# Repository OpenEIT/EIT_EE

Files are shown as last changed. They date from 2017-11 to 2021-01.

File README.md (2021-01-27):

# Spectra PDF

The schematic for the 32 electrode EIT system is called Spectra.pdf and is contained in the top level directory. Please let me know if you think it should have any modifications. 

# Eagle_EIT

Note: the following design is an older design for an 8 electrode system. I have a newer better system which was designed in Altium which I'll put up here as soon as crowd supply campaign finalized. In the meantime I'd love it if you wanted to join the mailing list! 

https://www.crowdsupply.com/mindseye-biomedical/spectra

## EIT PCB design in Eagle CAD

Electrical Impedance Tomography is a new way to image conductivity changes inside any mostly liquid medium - such as the human body. It's attractive as it doesn't use ionizing radiation like the X-rays used in a CATSCAN, and could be relatively cheap to mass produce. 

This project is an example of a working system from PCB to firmware to reconstruction algorithm. Further work could certainly improve the resolution, but for now we have functionality in all sub sections. 

This is everything required for the basic 8 electrode design to work. Photo of the assembled PCB included. 

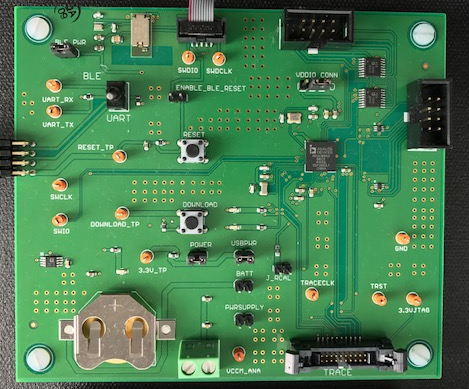
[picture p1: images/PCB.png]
EIT PCB


The design is based on the ADuCM350 which has a dedicated high precision front end with 16 bit resolution 160 kSPS data speed.The front end also performs a DFT at the rate of 13.8ms per calculation. This leads to a high performance minimal noise set up, excellent for both R&D or educational purposes. 

In the not too distant future kits may be available with a smaller version of the PCB mounted in a box, an electrode harness for mounting to the body, and all cables required to run. 

This combination would be an excellent educational tool for those researching this area, as it allows you to try most of the reconstruction algorithms or come up with your own and quantify any improvements in results. 

It's the same technique as is used in CATSCAN's, except the current running through the body instead of dangerous ionizing radiation of X-Rays. 

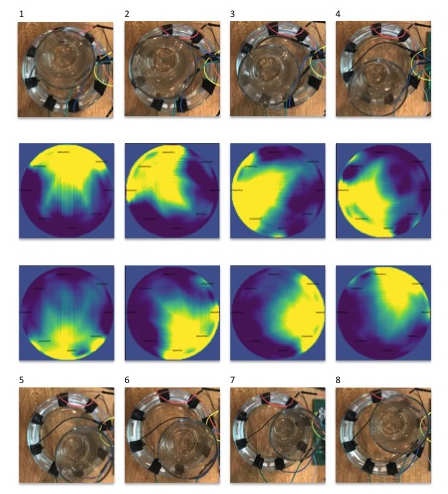
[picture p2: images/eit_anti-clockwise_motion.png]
EIT example


Improvements are welcome to this design. To increase resolution you could make a rotational version which is time resolution limited, or simply add more electrodes and re-compute the reconstruction that way. Another intended improvement is to move to tetrapolar differential electrodes set up. If you'd like to collaborate just pull the repository or email contact@mindseyebiomedical.com

We'd love to hear how you are using this! 

## New Board Design 

We have a newer better board design which is uploaded and called Spectra.pdf. Check it out. 

## Future Plans 

Are hatching! Join the technical discussion list to discuss further at openeit.github.io 

## License 

The Creative Commons Attribution-NonCommercial-ShareAlike 4.0 International License seems to fit best with this project. Check out the human readable summary here: 

<br />This work is licensed under a <a rel="license" href="http://creativecommons.org/licenses/by-nc-sa/4.0/">Creative Commons Attribution-NonCommercial-ShareAlike 4.0 International License</a>.

If you'd like to make a derivative of this project in a commercial setting, we'd love a payment so that we can afford to spend time both maintaining this project and making more projects like this one. If this hybrid open source model works, it would enable open source projects to receive some funding, making the global commons stronger to benefit everyone.

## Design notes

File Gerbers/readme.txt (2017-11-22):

board stackup

1. top layer
2. inner layer pwr
3. inner layer gnd
16. bottom layer

TOP SIDE  *.GTL
inner layer 2  *.G2L
inner layer 3  *.G3L
BOTTOM SIDE  *.GBL
silkscreen top side  *.GTO
solder stop mask top *.GTS
solder stop mask bottom *.GBS
cream frame top  *.GTC
board outline *.GKO
excellent drill file *.drd
component placement list top	  *.mnt
component placement list bottom *.mnb

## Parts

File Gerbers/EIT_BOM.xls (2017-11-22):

Qty-1 | Part References | Value | Package | Mfg Part Num | Mfg Name | VID | Vendor Part Num | Description | Pkg Code
1 | CR2032 |  | CR2032-SMD | 3002TR | Keystone Electronics | DK | 36-3002CT-ND | HOLDER BATTERY COIN 20MM DIA SMD | Surface Mount Coincell Holder
2 | AFE, M1 |  | 2X04SHROUDED | 61200821621 | Wurth Electronics | DK | 732-5395-ND | 8 Positions Header Shrouded Connector 0.100 2.54mm Through Hole | Through Hole
1 | PWRLED |  | 0603_LED | 150060BS75000 | Wurth Electronics | DK | 732-4966-1-ND | LED BLUE CLEAR 0603 SMD | 0603 1608 Metric
1 | LED2 |  | 0603_LED | 150060GS75000 | Wurth Electronics | DK | 732-4971-1-ND | LED GREEN CLEAR 0603 SMD | 0603 1608 Metric
1 | LED1 |  | 0603_LED | 150060YS75000 | Wurth Electronics | DK | 732-4981-1-ND | LED YELLOW CLEAR 0603 SMD | 0603 1608 Metric
1 | IC1 |  | TY-EYSGJN | EYSGJNAWY-1X | Taiyo Yuden | DK | 587-4378-1-ND | RF TXRX MOD BLUETOOTH TRACE ANT | BLE Module
7 | BATT, BLE_PWR, ENABLE_BLE_RESET, J_RCAL, POWER, PWRSUPPLY, USBPWR |  | 1X02 | M20-9990246 | Harwin | DK | 952-2262-ND | 2 Positions Header Unshrouded Breakaway Connector 0.100 Through Hole Tin | Through Hole Male 2 Pin
1 | XTAL1 |  | FC-12M | SER3673CT-ND | Epson | DK | FC-12M 32.7680KD-A3 | 32.768kHz Â±30ppm Crystal 12.5pF 90 kOhm | 2-SMD
2 | R2, R3 | 0 | RES1608X55 | MCR03EZPJ000 | Rohm Semiconductor | DK | RHM0.0GTR-ND | RES SMD 0.0OHM JUMPER 1-10W 0603 | 0603 1608 Metric
5 | C1, C8, C_VCCM2, RESET_CAP, VCCM_DIG | 0.1uF | CAPC1608X87N | GRM188R71C104KA01D | Murata Electronics North America | DK | 490-1532-2-ND | 0.10ÂµF 16V X7R Ceramic Capacitor | 0603 1608 Metric
2 | VBIAS, VDDIO | 0.47uF | CAPC1608X87N | GRM188R71E474KA12D | Murata Electronics North America | DK | 490-3291-2-ND | 0.47ÂµF 25V X7R Ceramic Capacitor | 0603 1608 Metric
1 | R1 | 1K | 0603-RES | MCR03ERTJ102 | Rohm Semiconductor | DK | RHM1.0KCGCT-ND | RES SMD 1K OHM 1-10W 0603 | 0603 1608 Metric
2 | C5, C7 | 1uF | CAPC1608X87N | GRM188R60J105KA01D | Murata Electronics North America | DK | 490-1550-1-ND | 1ÂµF 6.3V X5R Ceramic Capacitor | 0603 1608 Metric
1 | U$10 | 2X5_0.05"_CORTEX_DEBUGSMD_SHROUDED | 2X5_0.05"_SMD_SH | SHF-105-01-L-D-SM-LC | Samtec | DK | SAM8855-ND | 10 Positions Header Shrouded Connector 0.050 1.27mm Surface Mount Gold | SWD Connector SMT
1 | U$11 | 2X10_0.05"_CORTEX_DEBUG_WITH_ETMSMD_SHROUDED | 2X10_0.05"_SMD_SH | EHF-110-01-L-D-SM | Samtec | DK | SAM8210-ND | 20 Positions Header Shrouded Connector 0.050 1.27mm Surface Mount Gold | JTAG Connector SMT
2 | 3.3V_BOARDC, VREF | 4.7uF | CAPC1608X87N | GRM188R60J475ME19D | Murata Electronics North America | DK | 490-5421-1-ND | 4.7ÂµF 6.3V X5R Ceramic Capacitor | 0603 1608 Metric
2 | DOWNLOAD_R, RESETR | 10K | RES1608X55 | MCR03EZPFX1002 | Rohm Semiconductor | DK | RHM10.0KHCT-ND | RES SMD 10K OHM 1-10W 0603 | 0603 1608 Metric
3 | C2, C3, C_VCCM1 | 10uF | CAPC1608X87N | GRM188R60G106ME47D | Murata Electronics North America | DK | 490-3298-1-ND | 10ÂµF 4V X5R Ceramic Capacitor | 0603 1608 Metric
4 | C4, C6, C_X32, X_X32_2 | 15pF | CAPC1608X87N | GRM1885C1H150JA01D | Murata Electronics North America | DK | 490-1407-1-ND | 15pF 50V Ceramic Capacitor | 0603 1608 Metric
2 | C_X161, C_X162 | 24pF | CAPC1608X87N | GRM1885C1H240JA01D | Murata Electronics North America | DK | 490-1412-1-ND | 24pF 50V Ceramic Capacitor | 0603 1608 Metric
1 | C9 | 100uF | CAP2012X100N | GRM21BR60G107ME15L | Murata Electronics North America | DK | 490-10510-1-ND | 100ÂµF 4V Ceramic Capacitor | 0805 2012 Metric
2 | AVDD_TXRX, DVDDC | 470nF | CAPC1608X87N | GRM188R71E474KA12D | Murata Electronics North America | DK | 490-3291-2-ND | 0.47ÂµF 25V X7R Ceramic Capacitor | 0603 1608 Metric
3 | P_R2, RL1, RL2 | 560 | RES1608X55 | MCR03ERTF5600 | Rohm Semiconductor | DK | RHM560CFCT-ND | RES SMD 560 OHM 1-10W 0603 | 0603 1608 Metric
1 | L1 | 600 | CAPC1608X87N | BLM18HG601SN1D | Murata Electronics North America | DK | 490-1033-1-ND | FERRITE BEAD 600 OHM 1LN | 0603 1608 Metric
1 | U3 | ADUCM350 | ADUCM350_DUNCAN | ADUCM350BBCZ | Analog Devices | DK | ADUCM350BBCZ-ND | IC MCU 16BIT AFE 120BGA | Surface Mount 120-LFBGA CSPBGA
2 | U$1, U$2 | ESDPROTECTION-DSILC6-4XX | SOT-666 | DSILC6-4P6 | STMicroelectronics | DK | 497-5544-2-ND | TVS DIODE 5VWM SOT666 ESD DIODE | Surface Mount SOT-666
1 | VDDIO_CONN | JUMPER-3PTH | 1X03 | M20-9990345 | Harwin | DK | 952-2263-ND | 3 Positions Header Unshrouded Breakaway Connector 0.100 Through Hole Gold | Through Hole
1 | CONN3 | MKDSN2 | MKDSN2 | 1729128 | Phoenix Contact | DK | 277-1247-ND | CONN TERM BLOCK 2POS GREEN | Through Hole 2pin Power connector
2 | M_1, M_2 | MULTIPLEXER-ADG1608BRUZ | RU_16 | ADG1608BRUZ | Analog Devices | DK | ADG1608BRUZ-ND | IC MULTIPLEXER 8X1 16TSSOP | Surface Mount 16-TSSOP
1 | ADP3333 | REGULATOR-ADP3333ARMZ-3.3-R7 | SOP65P490X110-8N | ADP3333ARMZ-3.3-R7 | Analog Devices | DK | ADP3333ARMZ-3.3-R7CT-ND | IC REG LDO 3.3V 0.3A 8MSOP | Surface Mount 8-MSOP
1 | UART_SELECT | SWITCH-DPDT | SWITCH-G13AH | G22AP | NKK Switches | DK | 360-2791-ND | SWITCH TOGGLE DPDT 0.4VA 28V | SwitchDPDT
2 | DOWNLOAD, RESET | SWITCH-MOMENTARY-2PTH | TACTILE-PTH | 1825910-6 | TE Connectivity | DK | 450-1650-ND | Tactile Switch SPST-NO Top Actuated Through Hole | Through Hole Button
14 | 3.3VJTAG, 3.3V_TP, DOWNLOAD_TP, GND, RESET_TP, SWCLK, SWDCLK, SWDIO, SWIO, TRACECLK, TRST, UART_RX, UART_TX, VCCM_ANA | TEST_POINT-TEST_POINTMINI | TP-MINI | 5003 | Keystone Electronics | DK | 36-5003-ND | TEST POINT PC MINI .040D ORANGE | 0.040 Hole Diameter
1 | JP1 | VDDOUT | 2X04/90 | 61300821021 | Wurth Electronics | DK | 732-5353-ND | 8 Positions Header Unshrouded Connector 0.100 Through Hole Right Angle Gold | Through Hole Right Angle
1 | CR | XTAL-ECX-31B | XTAL-ECX-31B | ECS-.327-7-34B-TR | ECS | DK | XC1656CT-ND | 32.768kHz 20ppm Crystal 7pF 70 kOhm | 2-SMD
1 | CR2 | XTAL-TSX-3225 | TSX-3225 | FA-238 16.0000MB-K3 | EPSON | MOUSER | 732-FA238-16B-K3 | 16MHz 50ppm Crystal 10pF 80 Ohm | 4-SMD

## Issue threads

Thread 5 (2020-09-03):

### ISSUE TITLE
Spectra Altium

### ISSUE THREAD

**Issue by sam-richardson** [OpenEIT/EIT_EE#5]
Are the Altium files for  the most up to date PCB (Spectra) available?

**Comment by JeanRintoul** [comment]
they are not currently available. I intend to make a separate repository at some point in the future for them, but am unclear what level of support to also provide on this, as I am already supporting the dashboard, firmware etc. The repository here has an 8 electrode version, an example flex array and also the schematic of Spectra.pdf in this repository is that is up to date, and is the production version of the Spectra board containing all technical data. If you have a competent EE on hand, you will be able to recreate/alter it from this data.

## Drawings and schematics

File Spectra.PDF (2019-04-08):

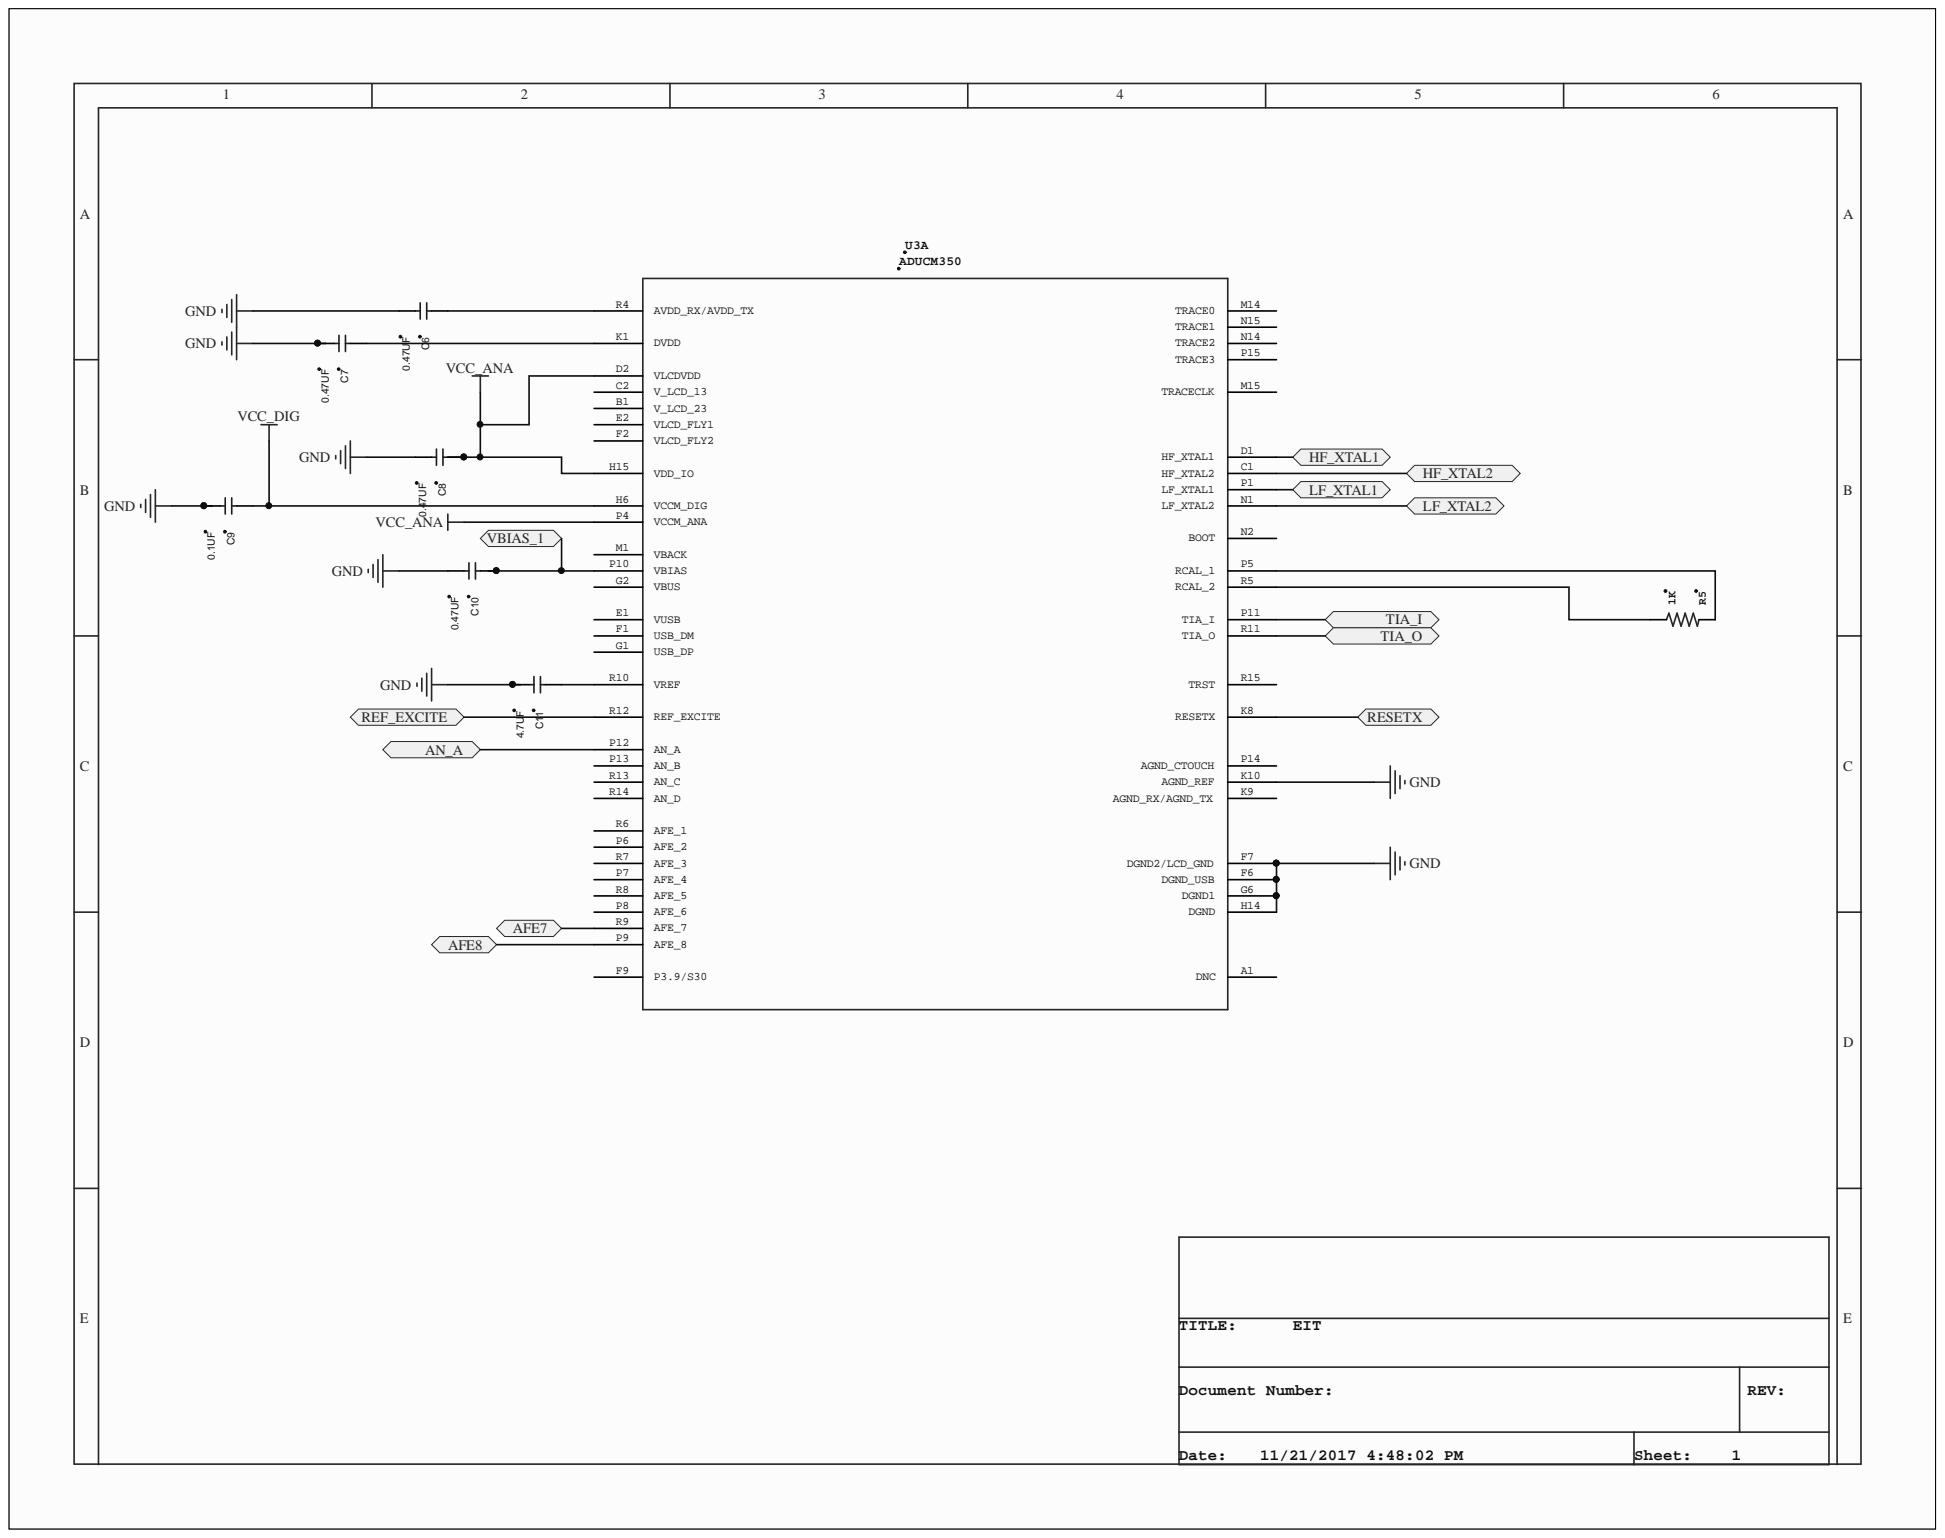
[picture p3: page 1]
TIA_I TIA_O

C 2
B 1 | | D 1 C 1

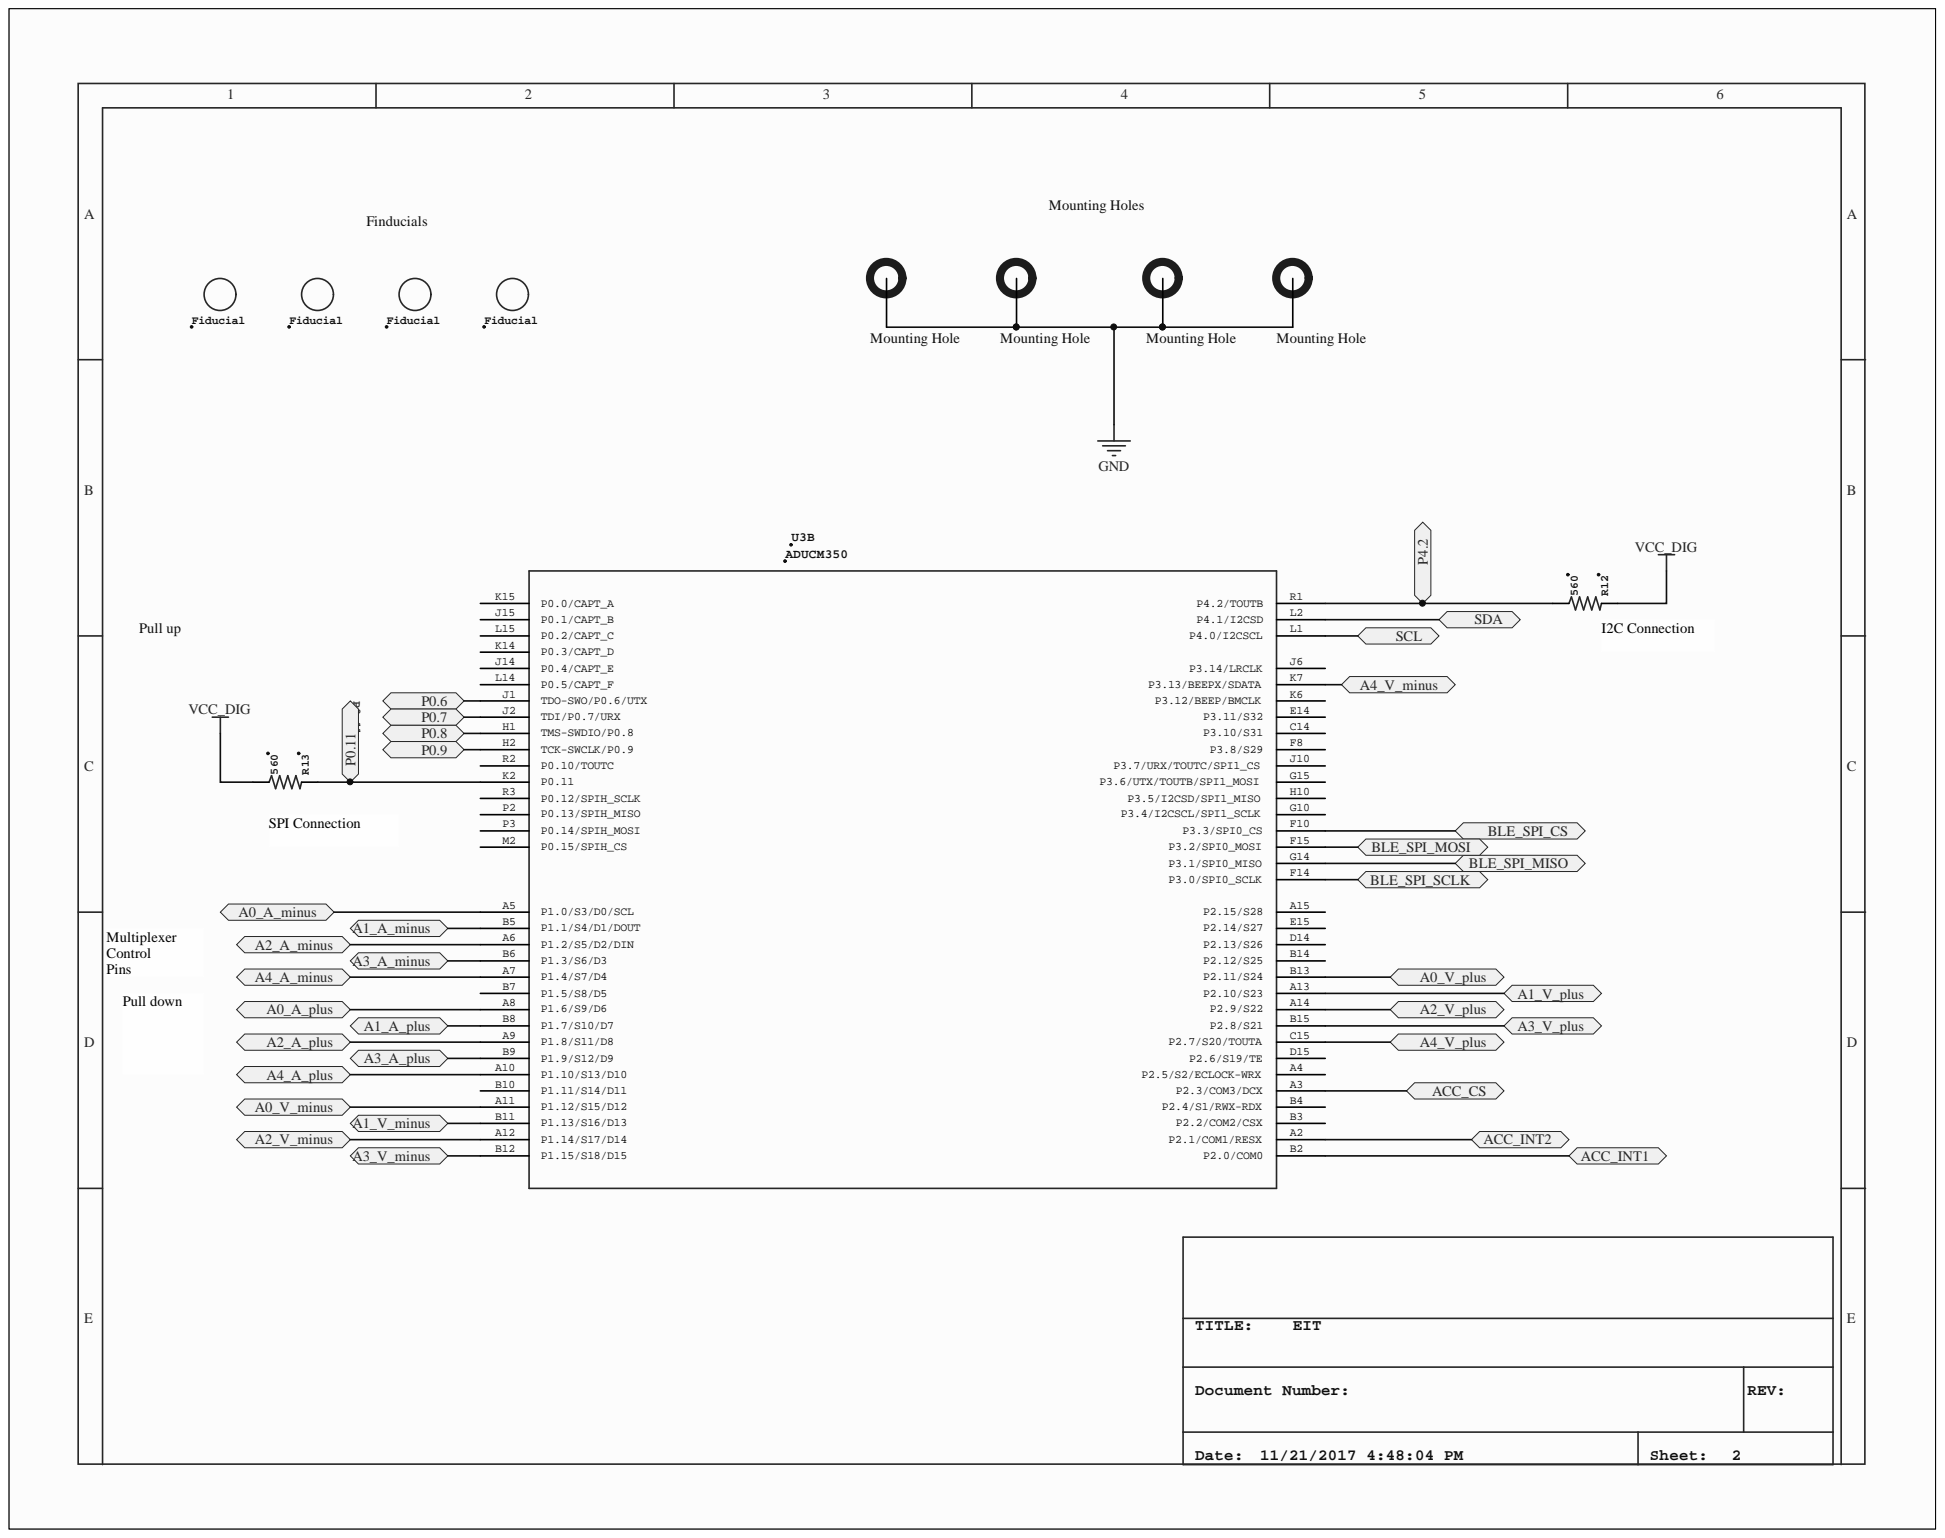
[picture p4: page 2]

Document Number: | REV:

Date: 11/21/2017 4:48:04 PM | Sheet: 2

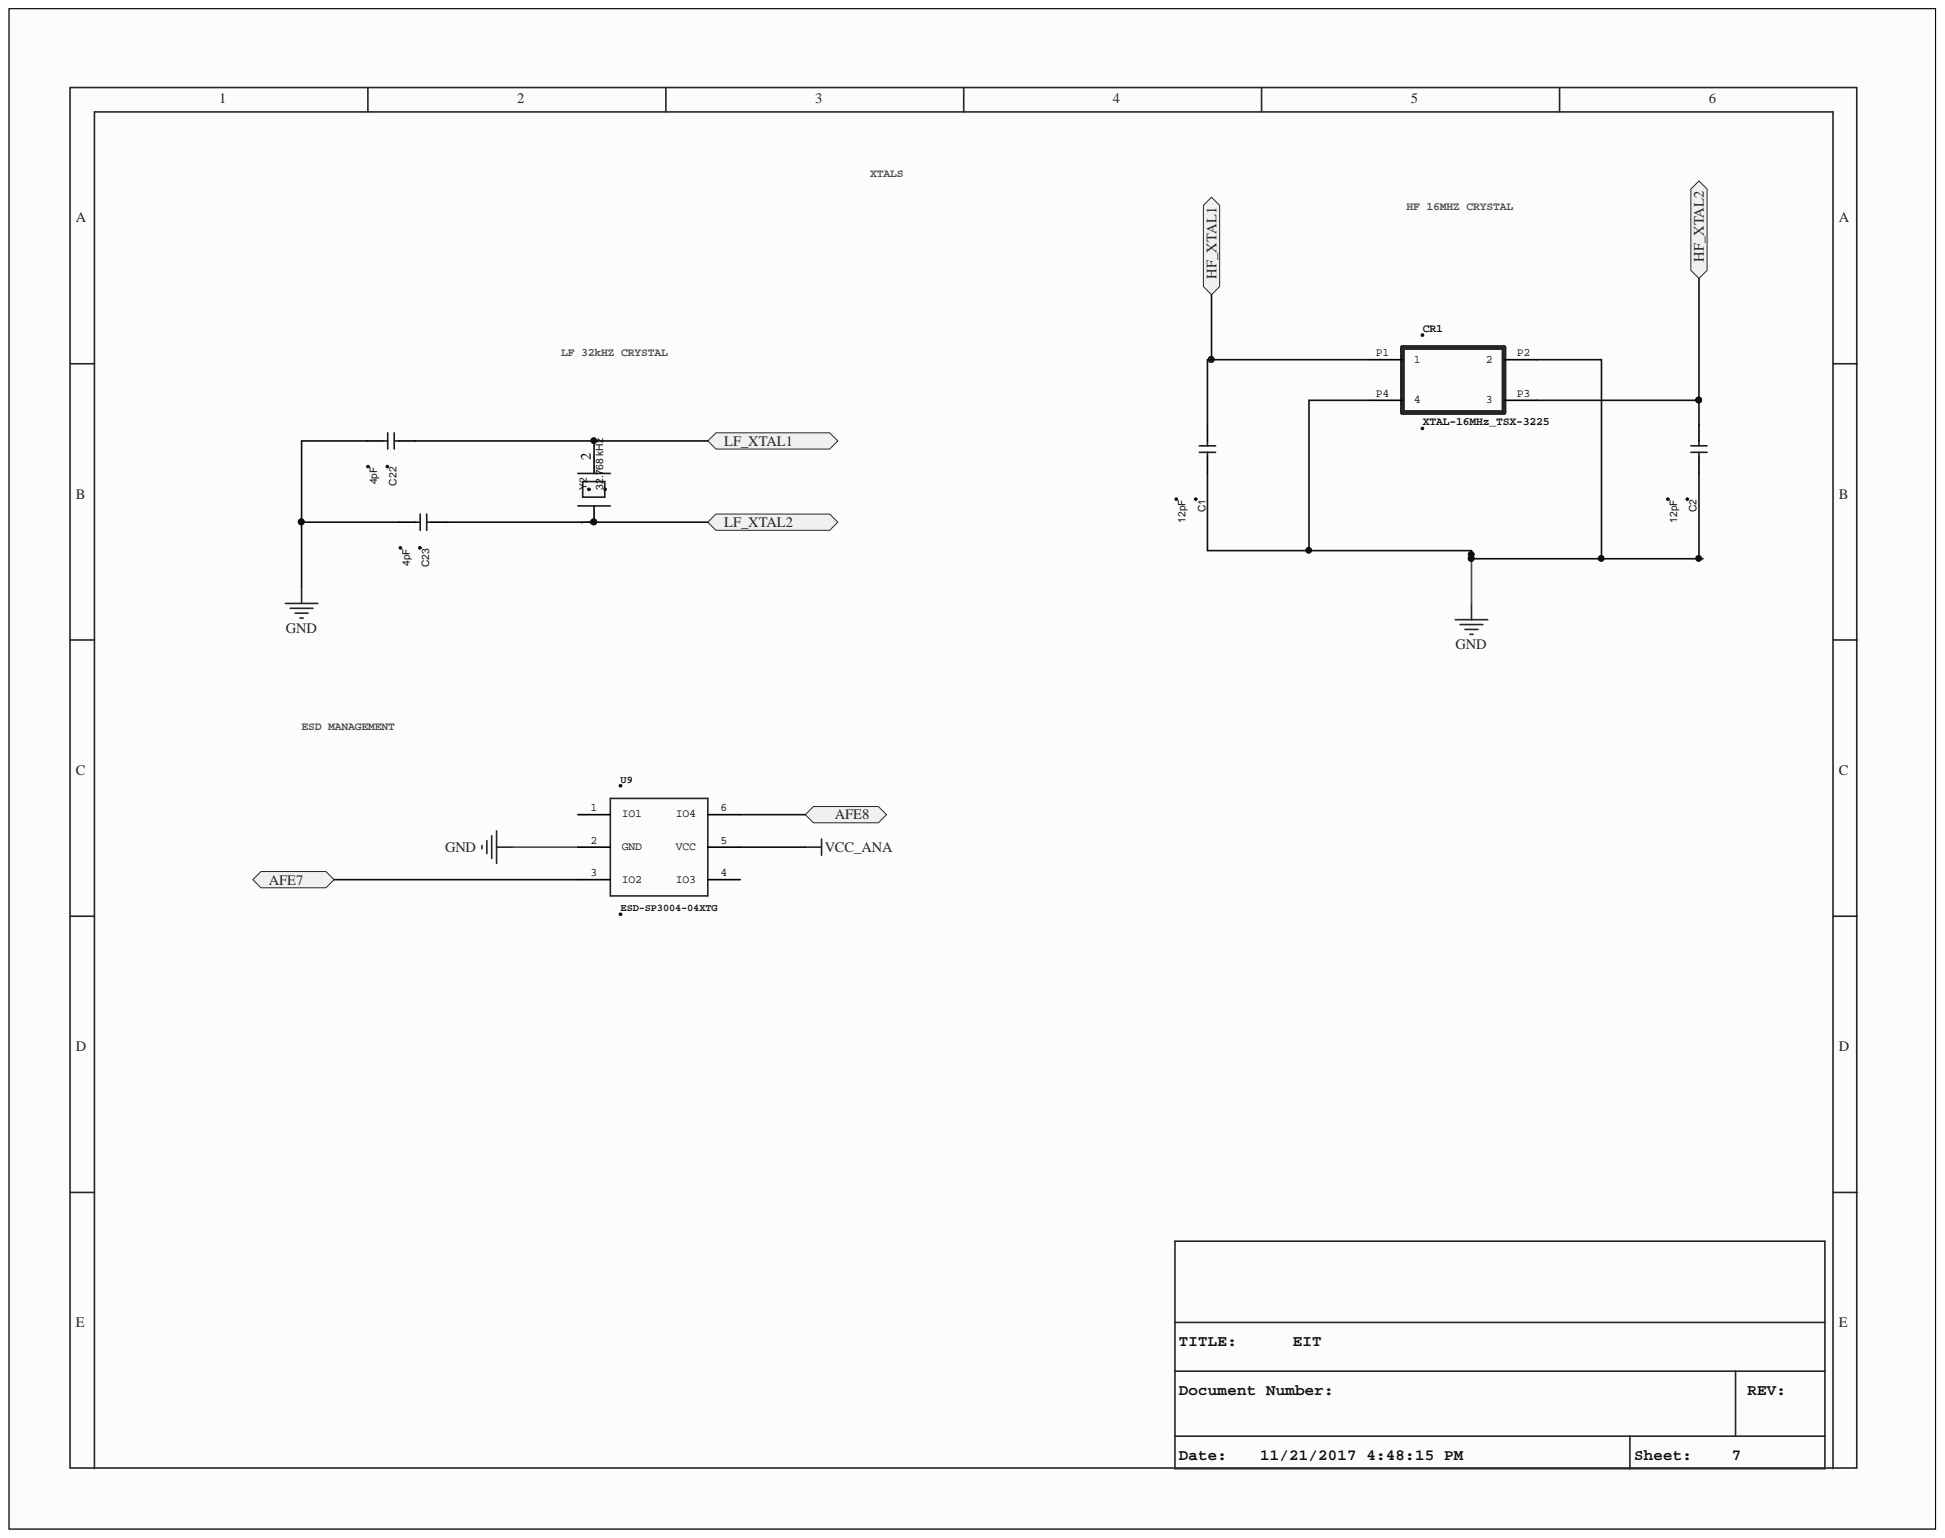
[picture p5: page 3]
32.768 kHz

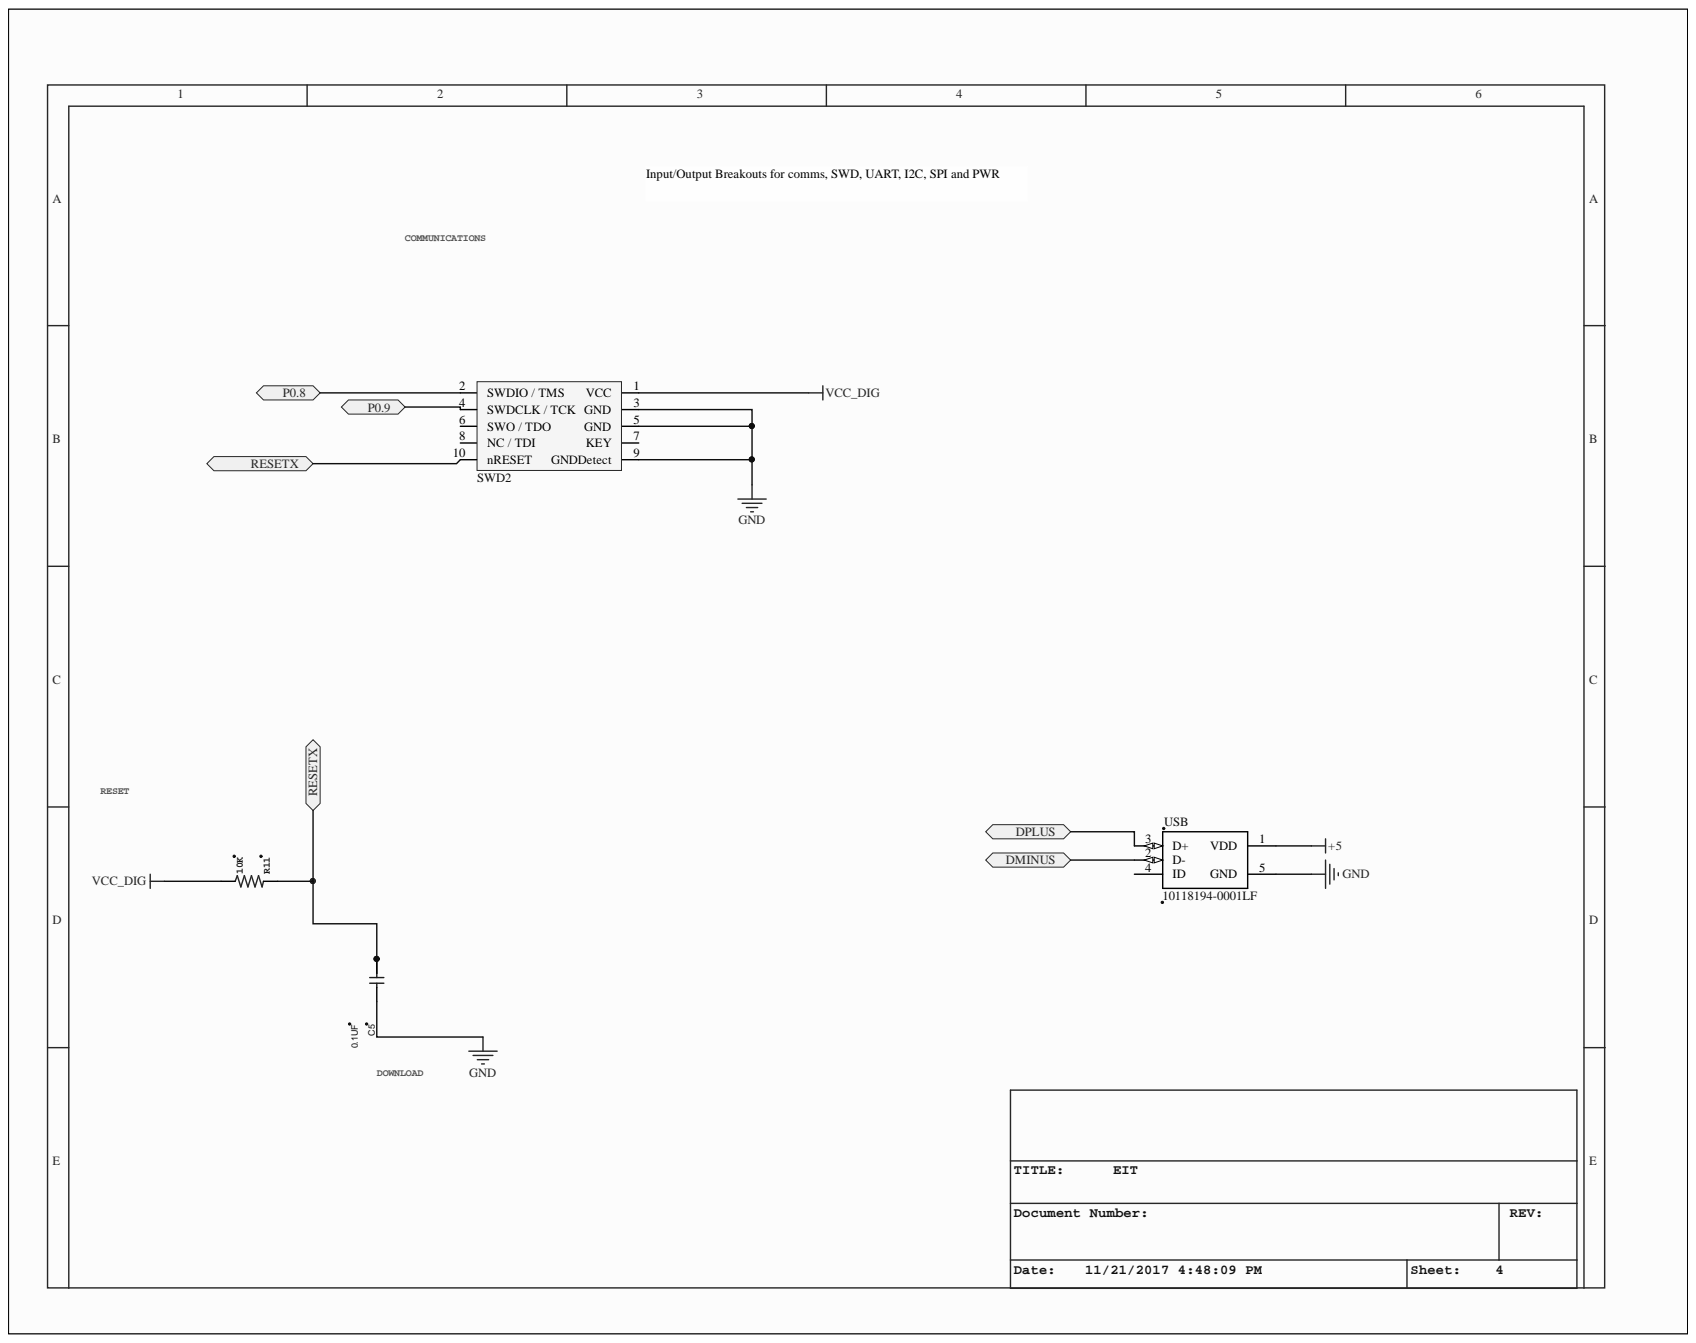
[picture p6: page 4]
VCC; 1 SWDIO / TMS 2; GND; 3 SWDCLK / TCK 4; 5 SWO / TDO 6; KEY; 7 NC / TDI 8; GNDDetect; 9 nRESET 10; GND 11

Input/Output Breakouts for comms, SWD, UART, I2C, SPI and PWR

Document Number: | REV:

Date: 11/21/2017 4:48:09 PM | Sheet: 4

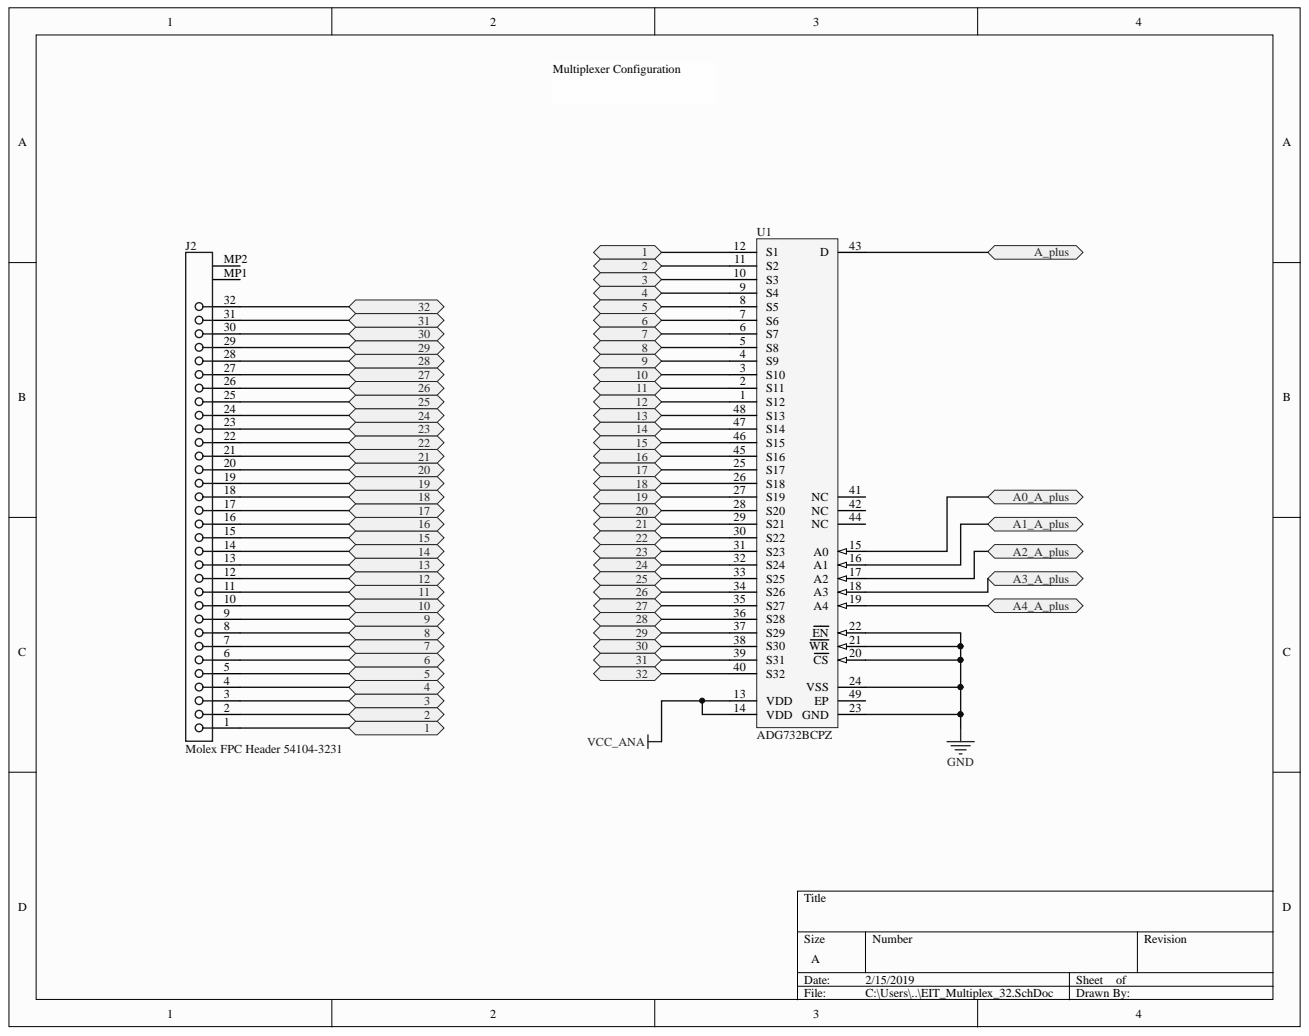
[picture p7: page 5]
A0_A_plus A1_A_plus A2_A_plus A3_A_plus A4_A_plus; exer Configura; VDD 14; 22 GND; 23 VSS; ader 54104-3231

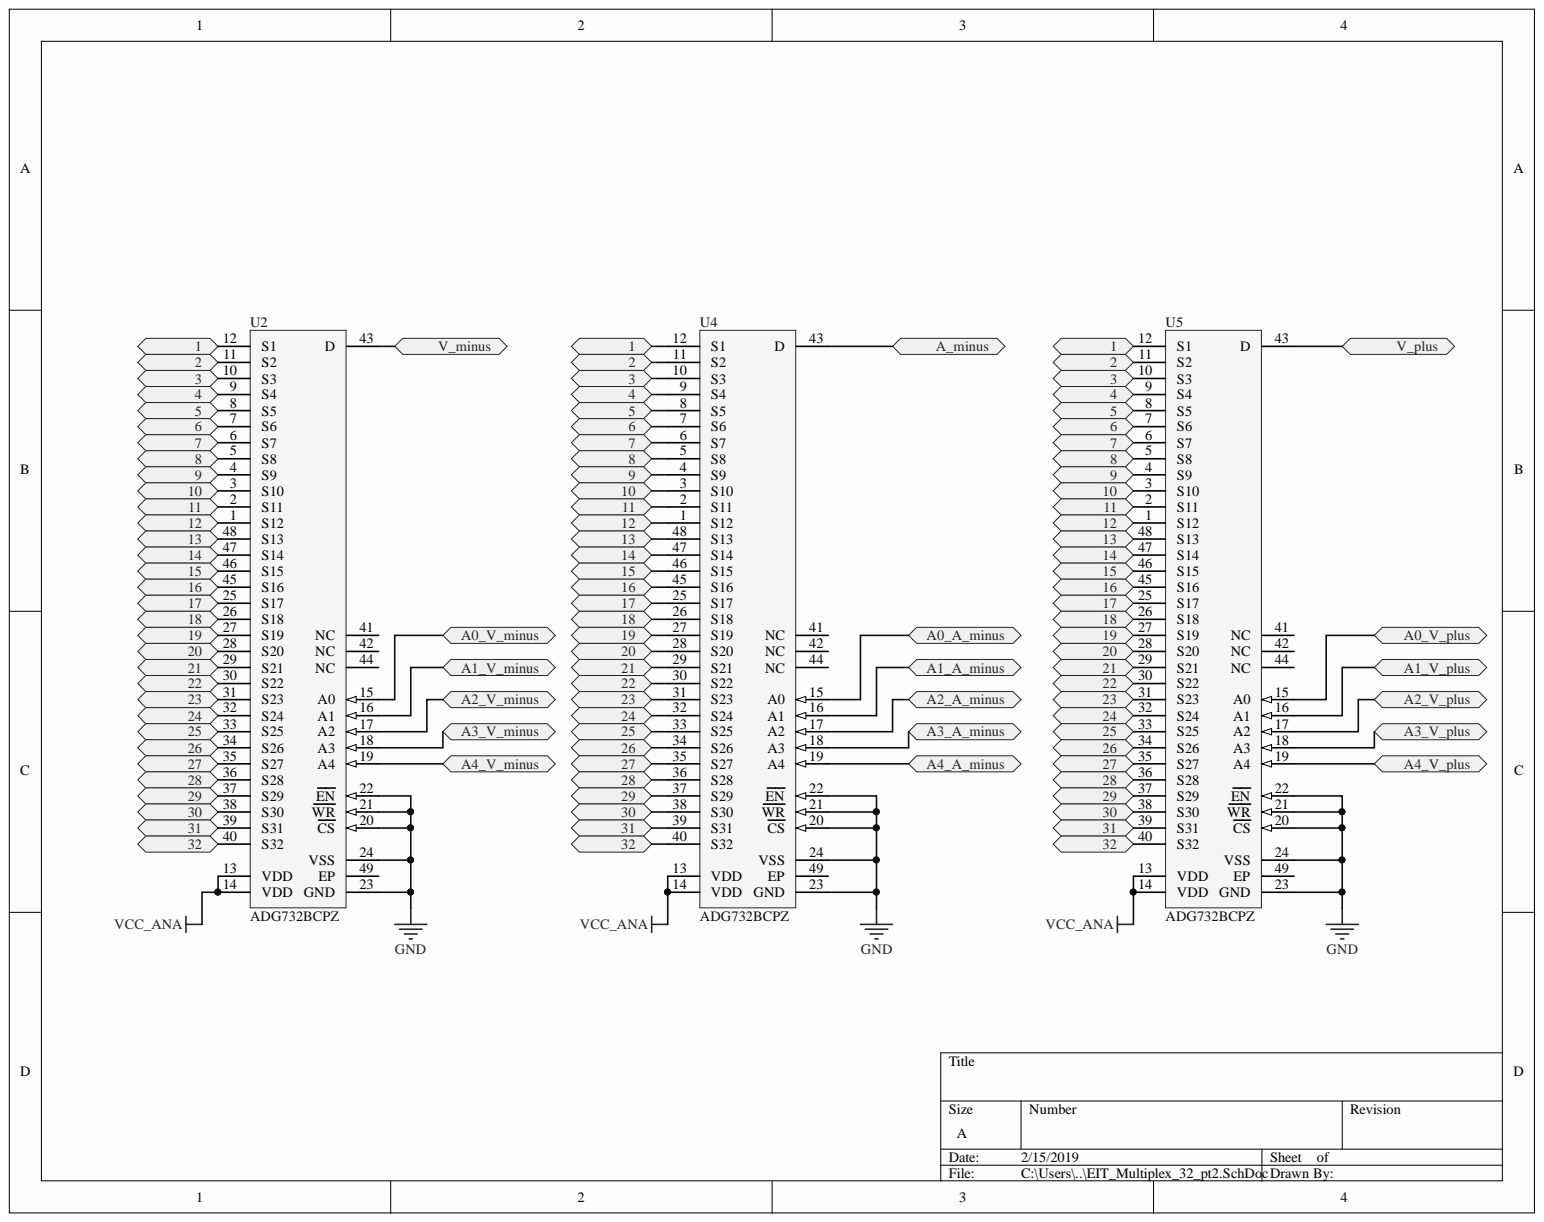
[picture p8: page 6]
Date:; Sheet of; File:; C:\Users\..\EIT_Multiplex_32_pt2.SchDocDrawn By:; VDD 13 VDD 14

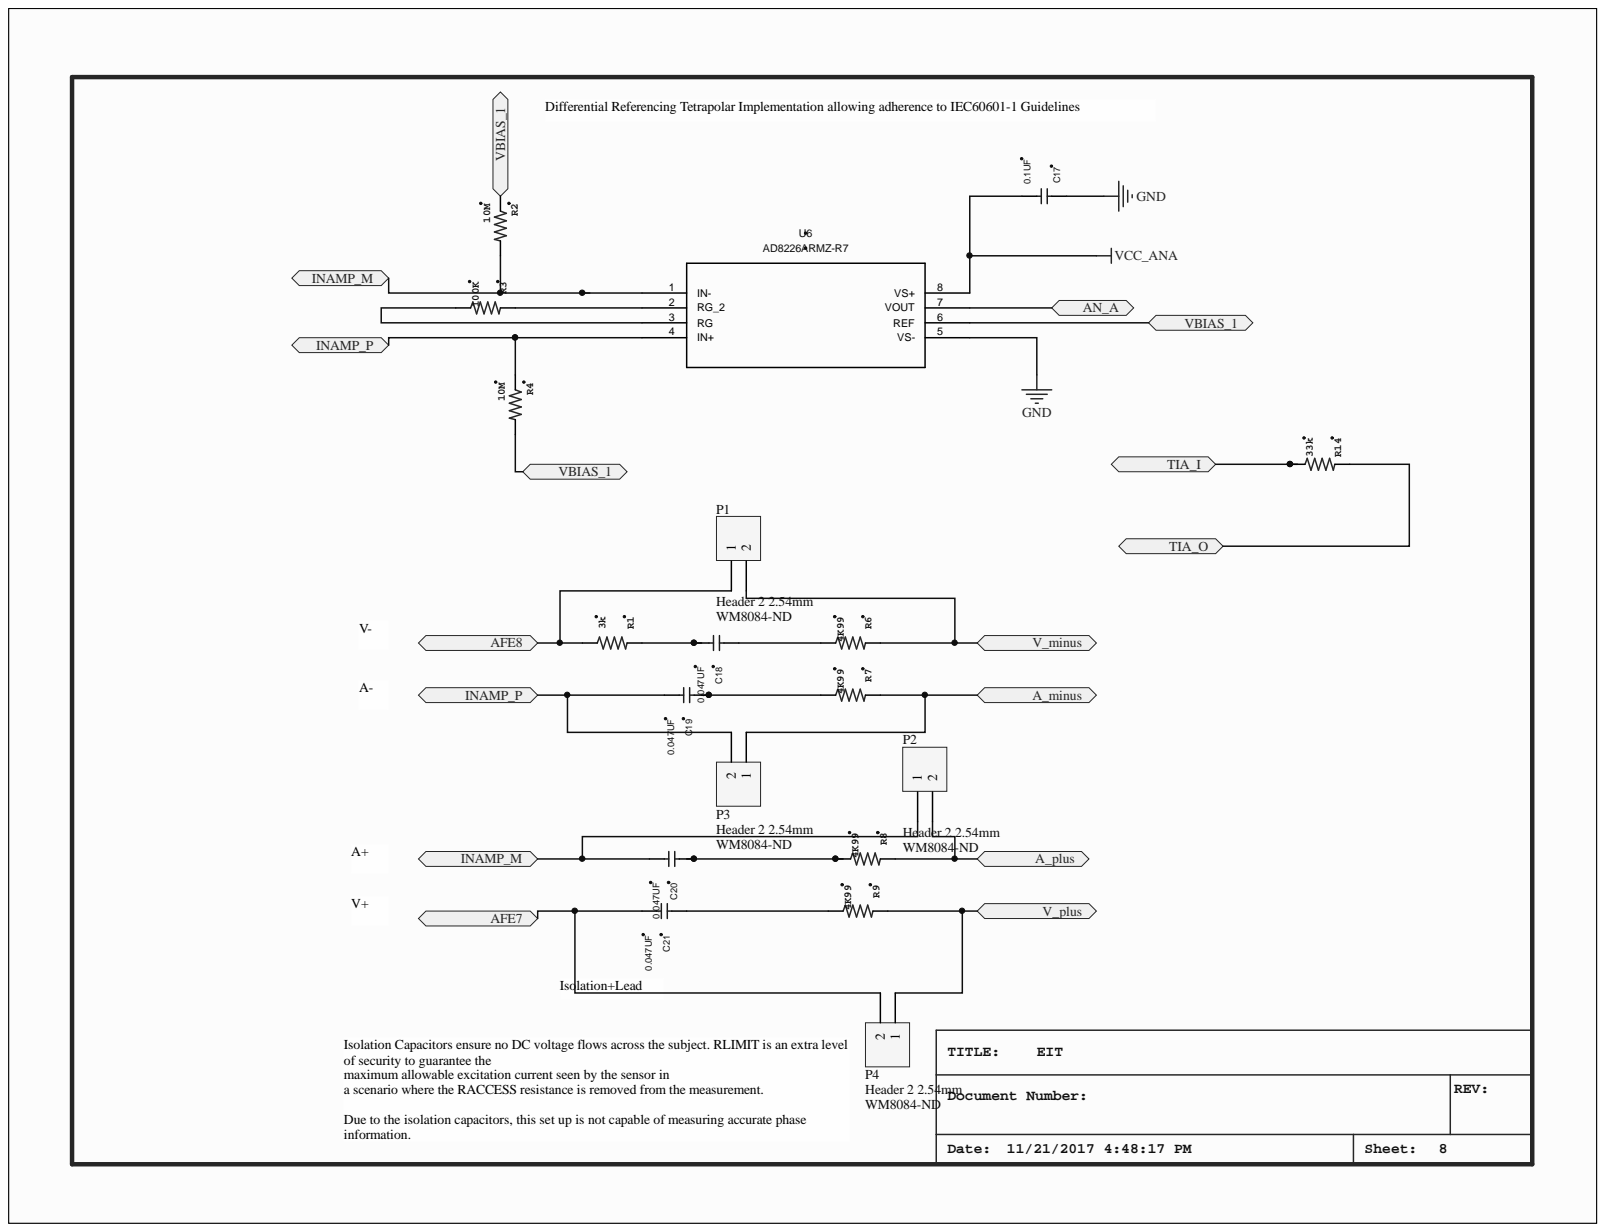
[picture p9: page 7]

Differential Referencing Tetrapolar Implementation allowing adherence to IEC60601-1 Guidelines

Isolation Capacitors ensure no DC voltage flows across the subject. RLIMIT is an extra level
of security to guarantee the
maximum allowable excitation current seen by the sensor in
a scenario where the RACCESS resistance is removed from the measurement.

Document Number: | REV:

Due to the isolation capacitors, this set up is not capable of measuring accurate phase
information.

Date: 11/21/2017 4:48:17 PM | Sheet: 8

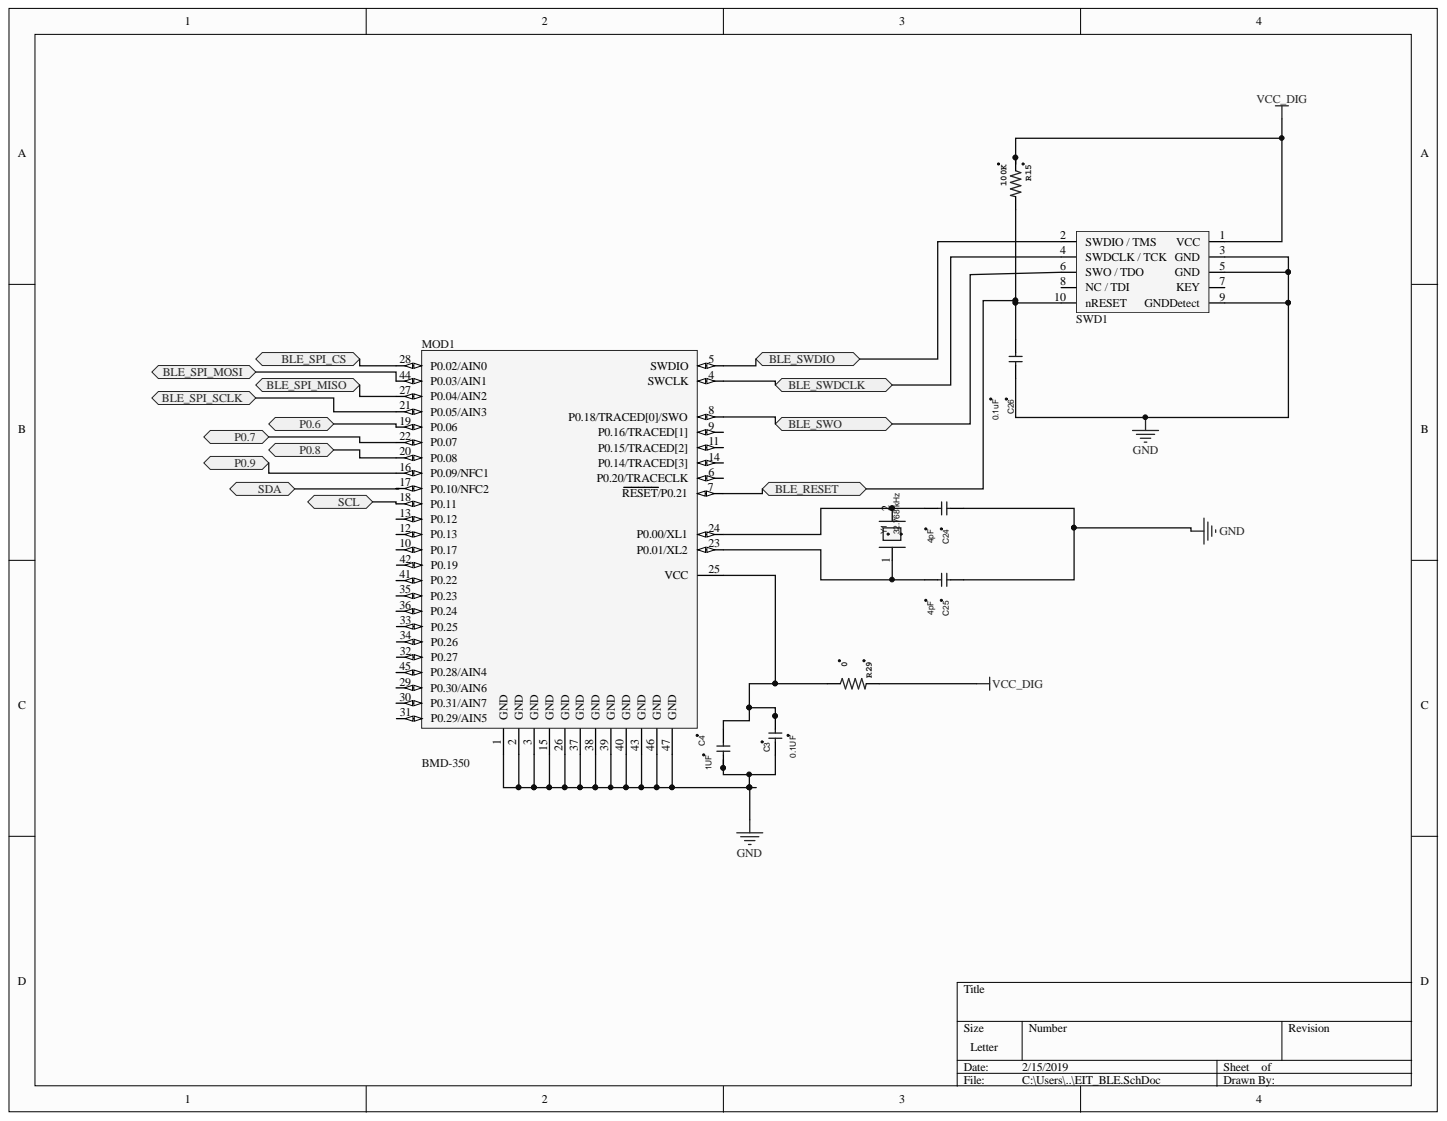
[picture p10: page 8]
Sheet o; GND 1; GND 2; GND 3; GND 15; GND 26; GND 39; GND 37; GND 38; GND 47; GND 46; GND 40; GND 43; 4 SWDIO; 32.768 kHz; 1 SWDIO / TMS 3 SWDCLK / TCK 5 SWO / TDO

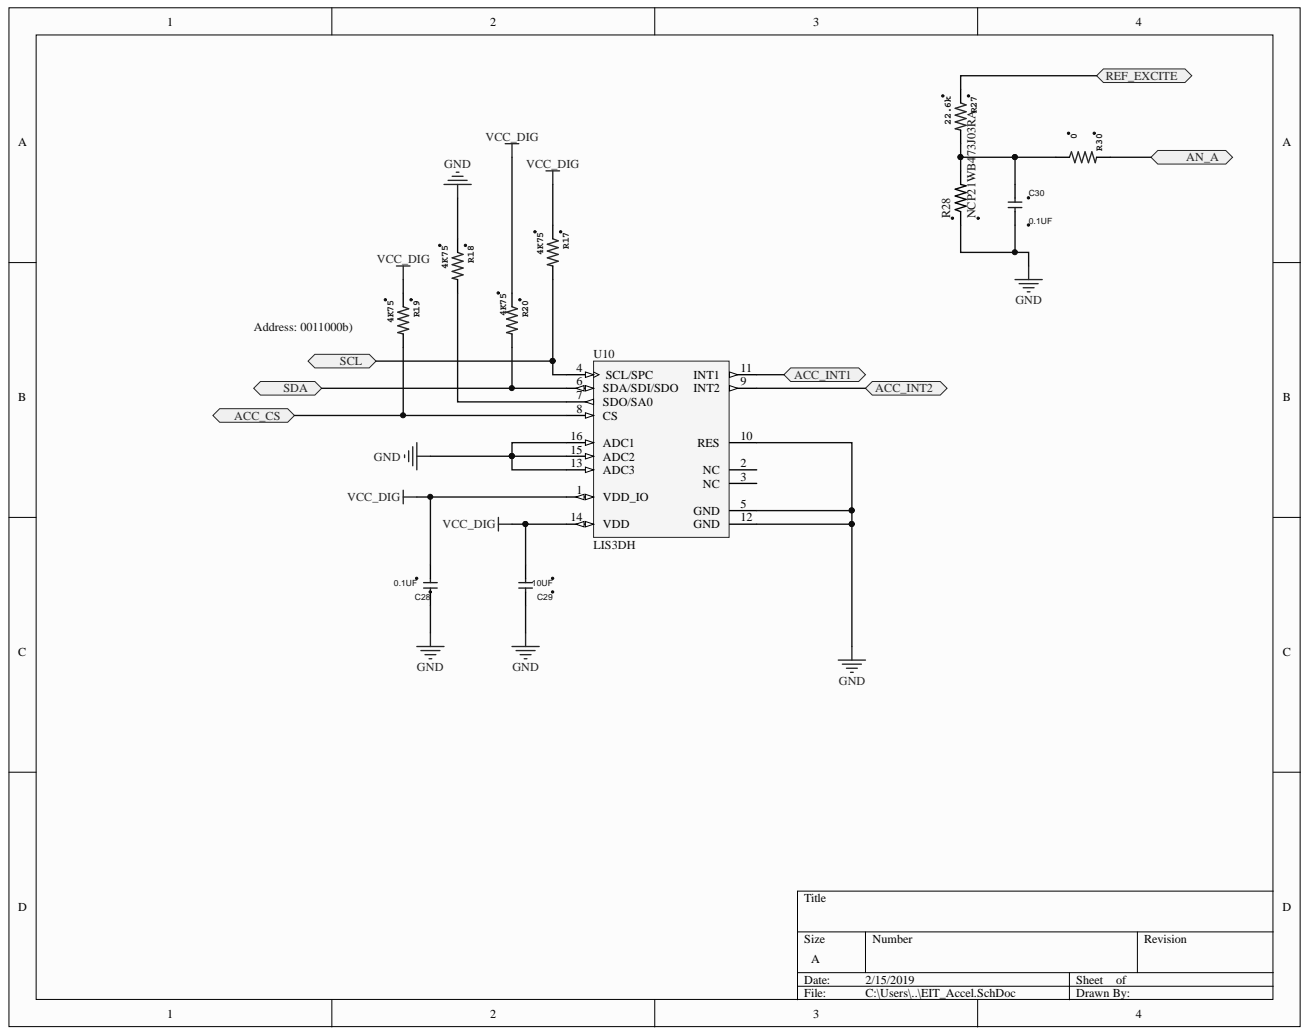
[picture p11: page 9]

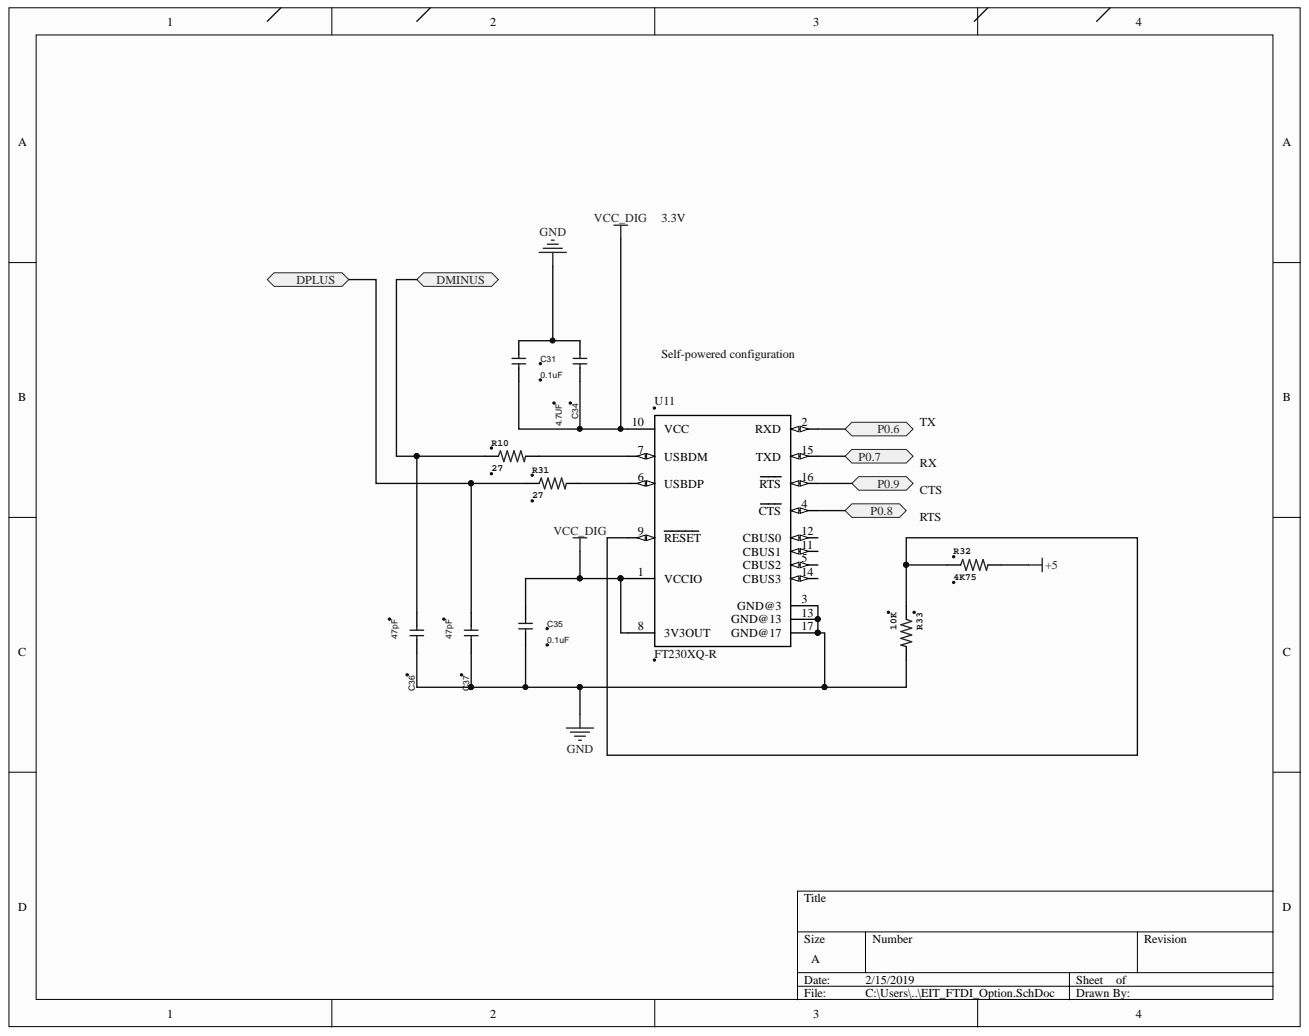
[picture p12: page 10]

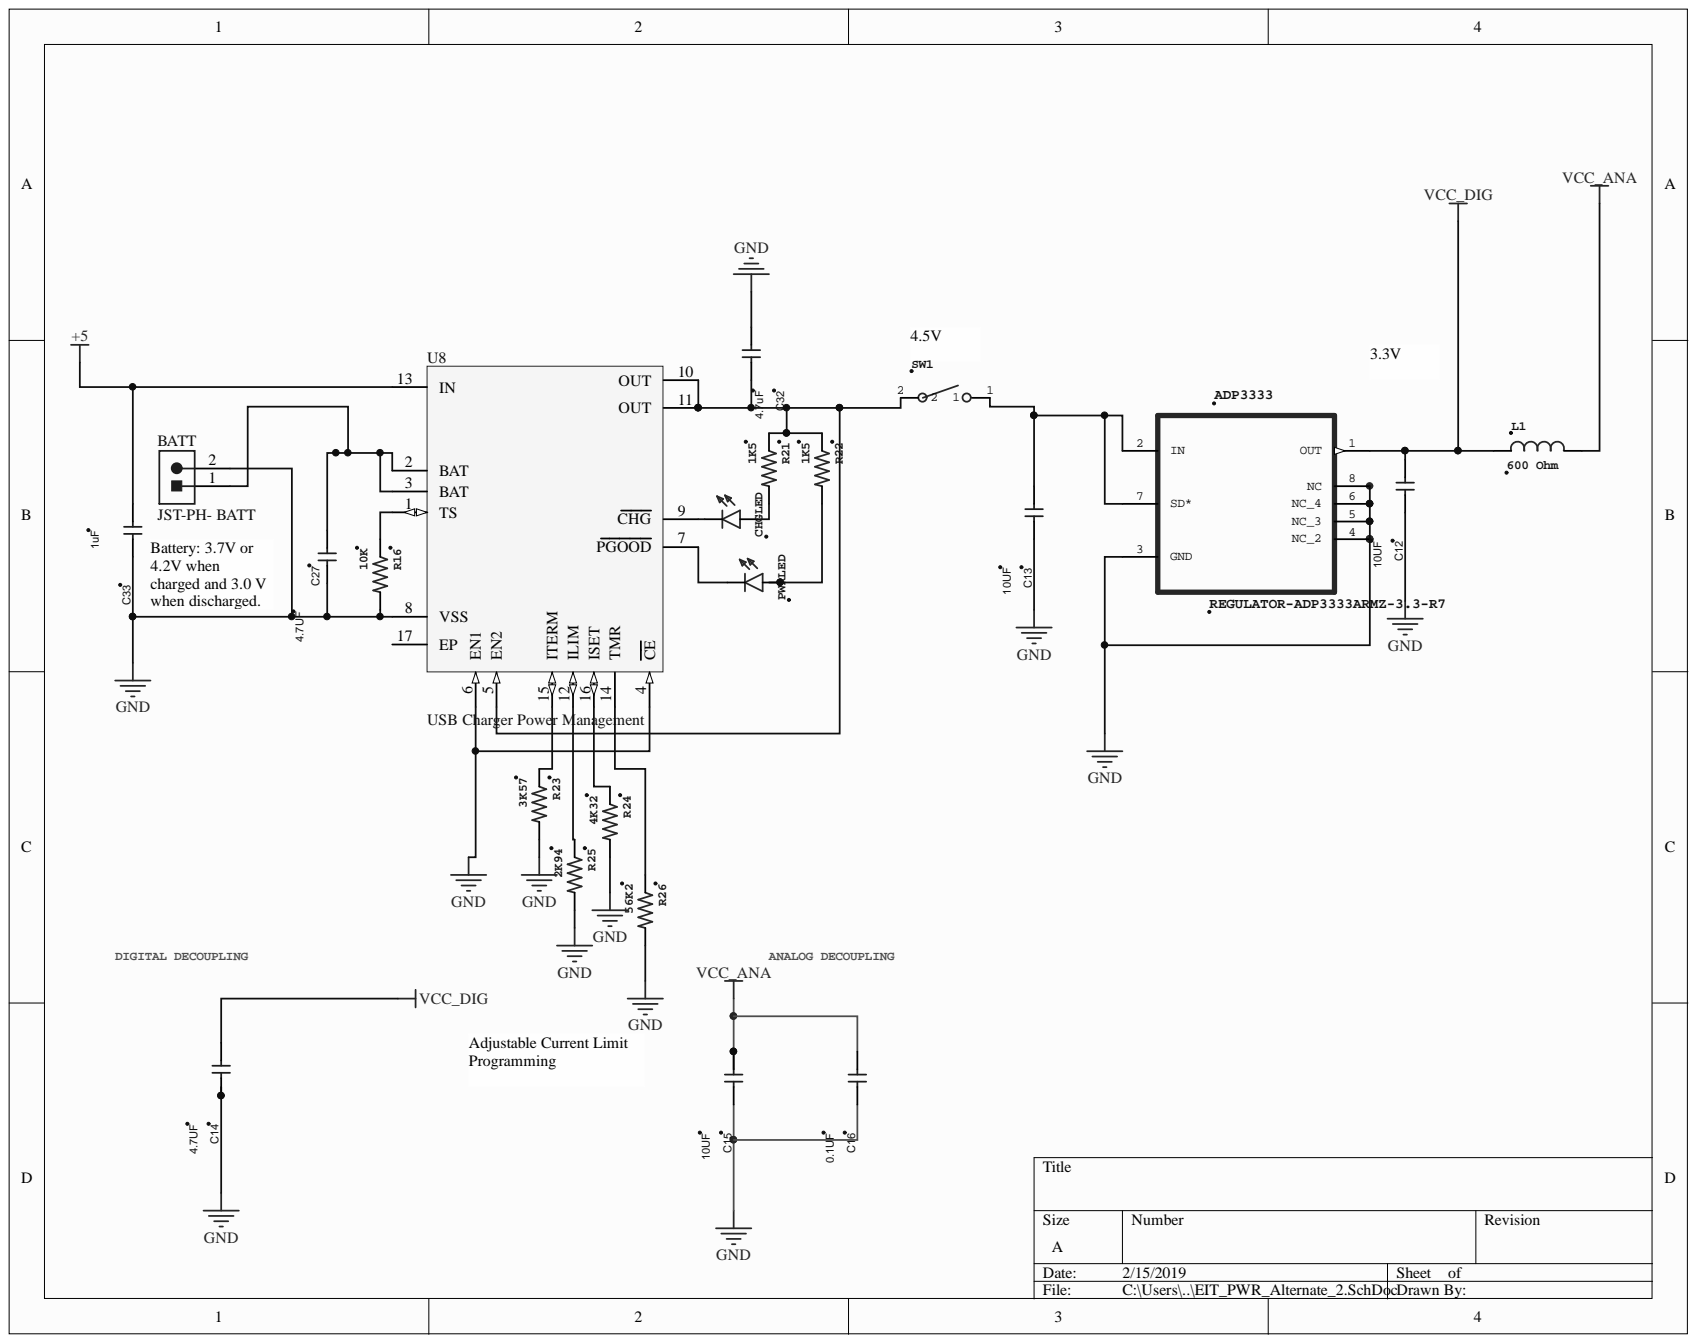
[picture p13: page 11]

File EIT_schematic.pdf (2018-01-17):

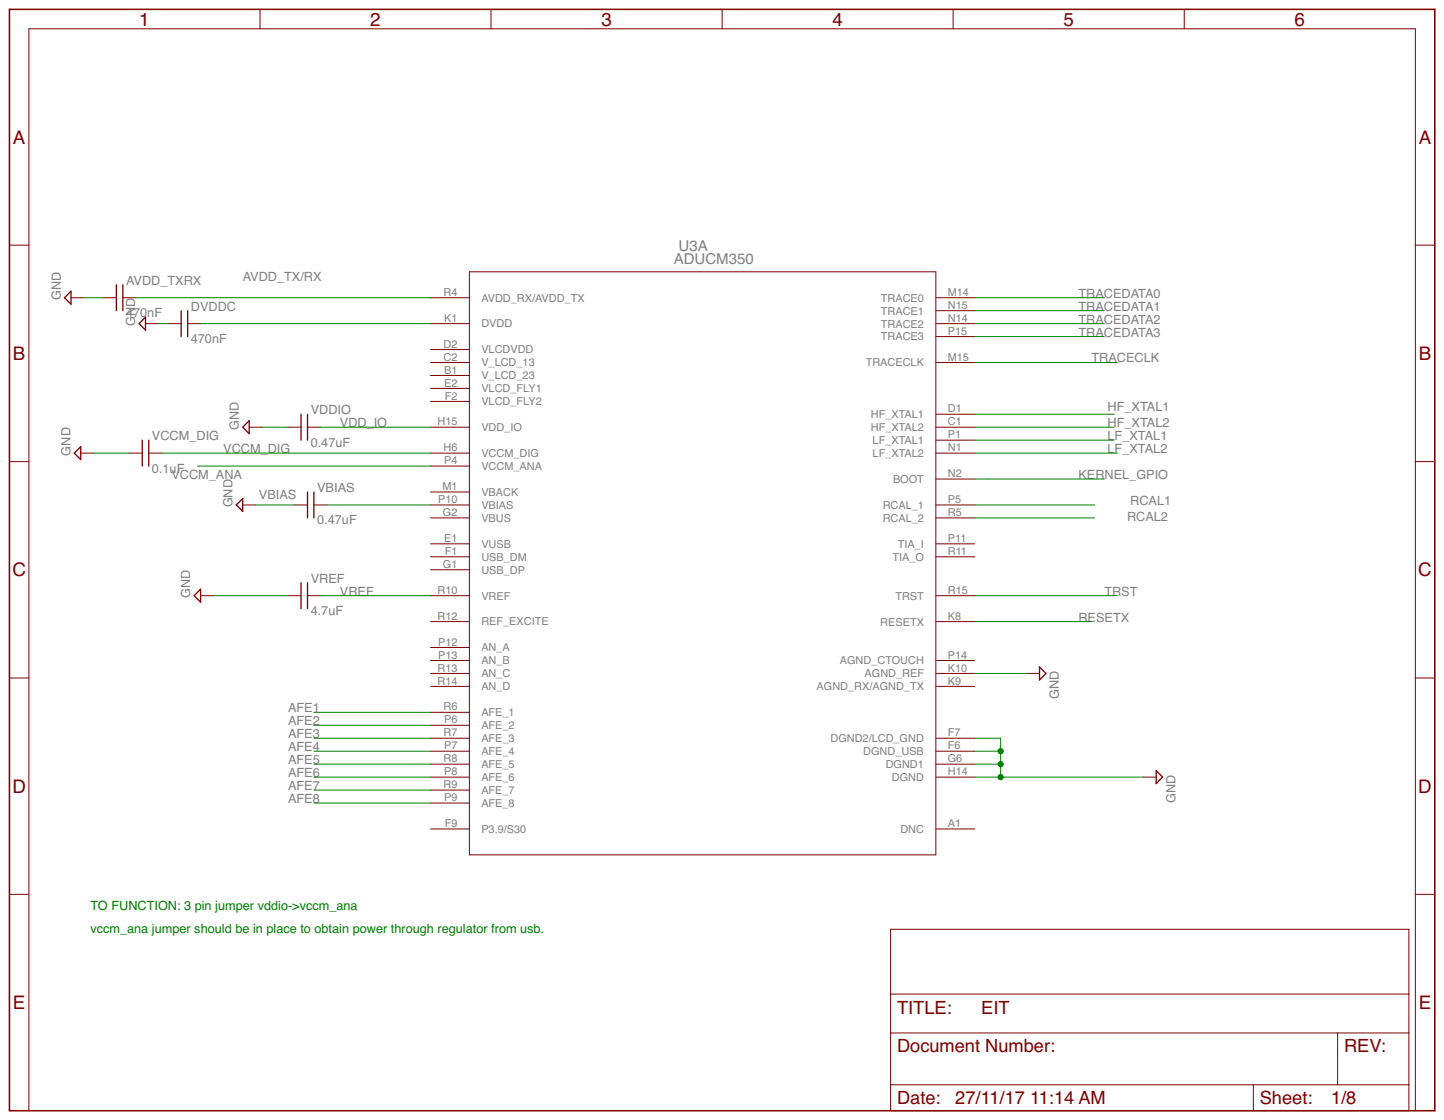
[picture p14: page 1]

TO FUNCTION: 3 pin jumper vddio->vccm_ana
vccm_ana jumper should be in place to obtain power through regulator from usb.

Document Number: | REV:

Date: 27/11/17 11:14 AM | Sheet: 1/8







VDD_IO - default position is M5 -position A, VDD_IO -> VCCM_ANA




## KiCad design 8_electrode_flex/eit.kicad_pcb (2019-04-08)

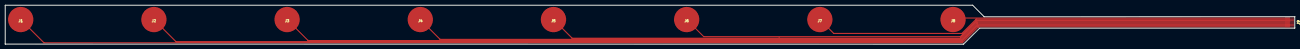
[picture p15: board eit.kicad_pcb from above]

Board: 2 copper layers, 509.4 x 15.4 mm, 9 parts (0 on the bottom side), 8 nets.

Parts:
J1, J2, J3, J4, J5, J6, J7, J8: TEST_1P; electrode10mm
J9: Conn_01x08; fpc-0.5mm-8p

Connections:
unnamed: J1.1, J9.1
unnamed: J2.1, J9.2
unnamed: J3.1, J9.3
unnamed: J4.1, J9.4
unnamed: J5.1, J9.5
unnamed: J6.1, J9.6
unnamed: J7.1, J9.7
unnamed: J8.1, J9.8

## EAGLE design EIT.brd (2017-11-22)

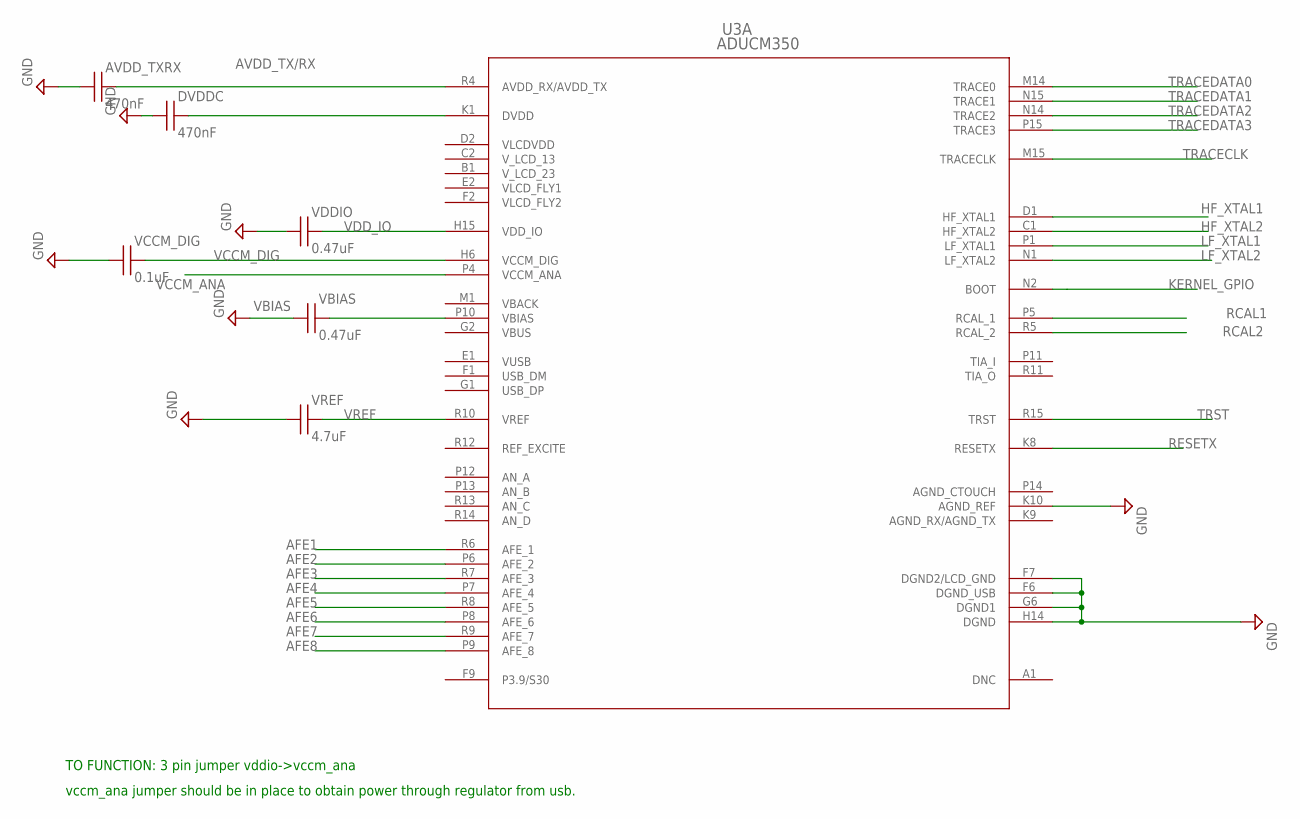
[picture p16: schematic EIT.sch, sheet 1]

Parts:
AVDD_TXRX: 470nF; CAPC1608X87N; MPN MCTEA4R7M1HB-0512P
DVDDC: 470nF; CAPC1608X87N; MPN MCTEA4R7M1HB-0512P
U3: ADUCM350; ADUCM350_DUNCAN; MPN ADUCM350BBCZ
VBIAS: 0.47uF; CAPC1608X87N; MPN JMK105BJ474KV-F
VCCM_DIG: 0.1uF; CAPC1608X87N; MPN MC0402X104K100CT
VDDIO: 0.47uF; CAPC1608X87N; MPN JMK105BJ474KV-F
VREF: 4.7uF; CAPC1608X87N; MPN GRM188R60J475ME19D

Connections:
AFE1: U3.R6 (AFE_1); also elsewhere on the board
AFE2: U3.P6 (AFE_2); also elsewhere on the board
AFE3: U3.R7 (AFE_3); also elsewhere on the board
AFE4: U3.P7 (AFE_4); also elsewhere on the board
AFE5: U3.R8 (AFE_5); also elsewhere on the board
AFE6: U3.P8 (AFE_6); also elsewhere on the board
AFE7: U3.R9 (AFE_7); also elsewhere on the board
AFE8: U3.P9 (AFE_8); also elsewhere on the board
AVDD_TX/RX: AVDD_TXRX.2, U3.R4 (AVDD_RX/AVDD_TX)
GND: AVDD_TXRX.1, DVDDC.1, U3.F6 (DGND_USB), U3.F7 (DGND2/LCD_GND), U3.G6 (DGND1), U3.H14 (DGND), U3.K10 (AGND_REF), VBIAS.1, VCCM_DIG.1, VDDIO.1, VREF.1; also elsewhere on the board
HF_XTAL1: U3.D1 (HF_XTAL1); also elsewhere on the board
HF_XTAL2: U3.C1 (HF_XTAL2); also elsewhere on the board
KERNEL_GPIO: U3.N2 (BOOT); also elsewhere on the board
LF_XTAL1: U3.P1 (LF_XTAL1); also elsewhere on the board
LF_XTAL2: U3.N1 (LF_XTAL2); also elsewhere on the board
RCAL1: U3.P5 (RCAL_1); also elsewhere on the board
RCAL2: U3.R5 (RCAL_2); also elsewhere on the board
RESETX: U3.K8 (RESETX); also elsewhere on the board
TRACECLK: U3.M15 (TRACECLK); also elsewhere on the board
TRACEDATA0: U3.M14 (TRACE0); also elsewhere on the board
TRACEDATA1: U3.N15 (TRACE1); also elsewhere on the board
TRACEDATA2: U3.N14 (TRACE2); also elsewhere on the board
TRACEDATA3: U3.P15 (TRACE3); also elsewhere on the board
TRST: U3.R15 (TRST); also elsewhere on the board
VBIAS: U3.P10 (VBIAS), VBIAS.2
VCCM_ANA: U3.P4 (VCCM_ANA); also elsewhere on the board
VCCM_DIG: U3.H6 (VCCM_DIG), VCCM_DIG.2
VDD_IO: U3.H15 (VDD_IO), VDDIO.2; also elsewhere on the board
VLCDVDD: DVDDC.2, U3.K1 (DVDD)
VREF: U3.R10 (VREF), VREF.2

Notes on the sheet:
TO FUNCTION: 3 pin jumper vddio->vccm_ana
vccm_ana jumper should be in place to obtain power through regulator from usb.

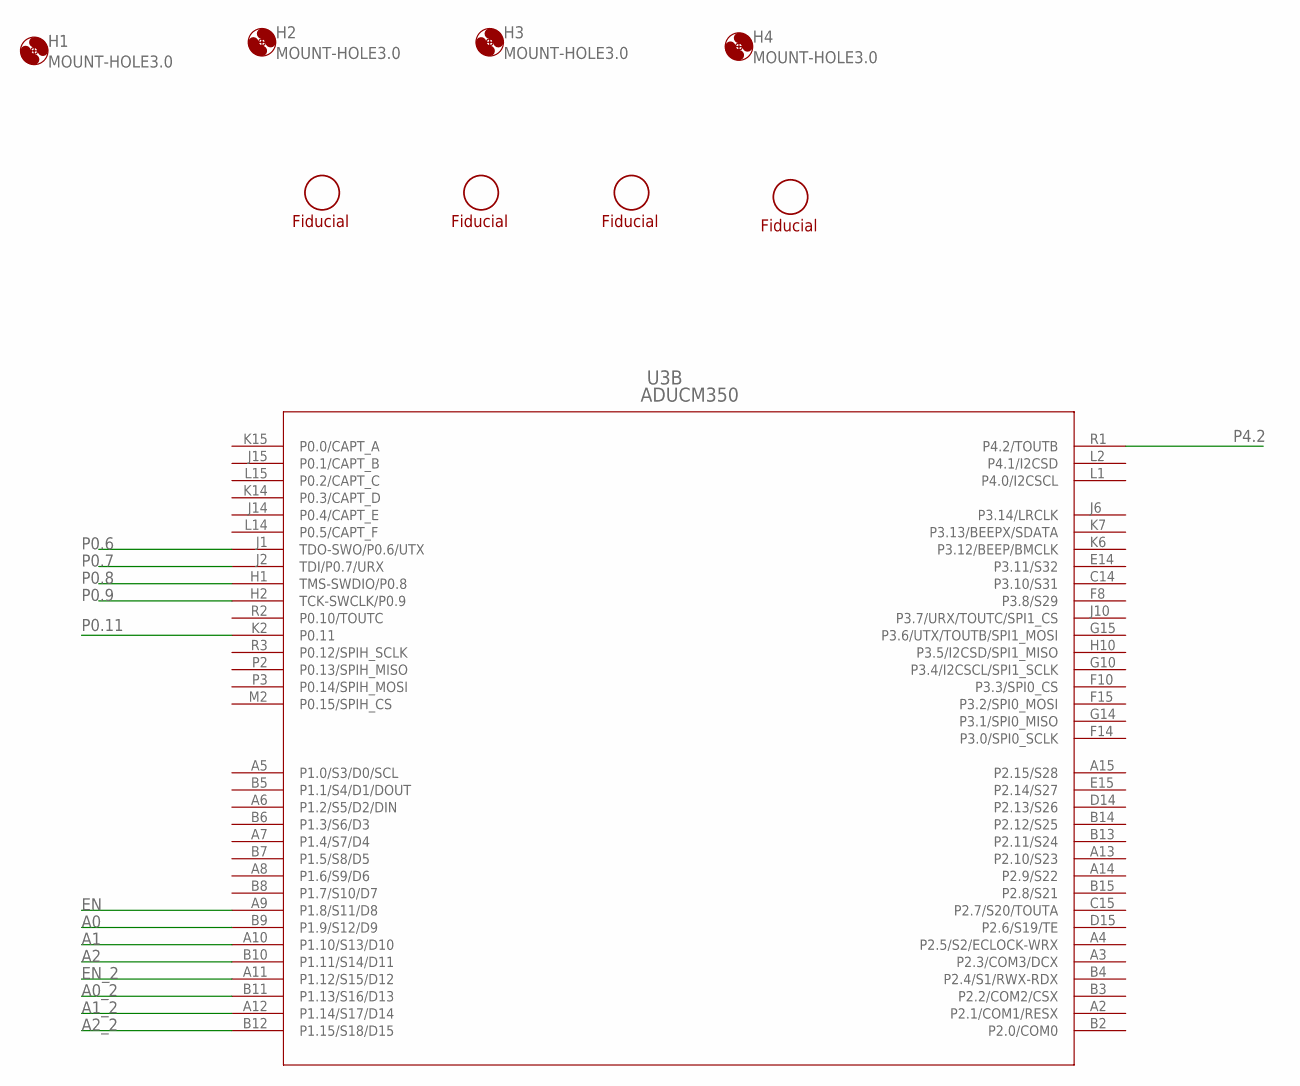
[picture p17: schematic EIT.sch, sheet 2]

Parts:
F1, F2, F3, F4: FIDUCIAL; FIDUCIAL-1MM
H1, H2, H3, H4: MOUNT-HOLE3.0; 3,0
U3: ADUCM350; ADUCM350_DUNCAN; MPN ADUCM350BBCZ

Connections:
A0: U3.B9 (P1.9/S12/D9); also elsewhere on the board
A0_2: U3.B11 (P1.13/S16/D13); also elsewhere on the board
A1: U3.A10 (P1.10/S13/D10); also elsewhere on the board
A1_2: U3.A12 (P1.14/S17/D14); also elsewhere on the board
A2: U3.B10 (P1.11/S14/D11); also elsewhere on the board
A2_2: U3.B12 (P1.15/S18/D15); also elsewhere on the board
EN: U3.A9 (P1.8/S11/D8); also elsewhere on the board
EN_2: U3.A11 (P1.12/S15/D12); also elsewhere on the board
P0.6: U3.J1 (TDO-SWO/P0.6/UTX); also elsewhere on the board
P0.7: U3.J2 (TDI/P0.7/URX); also elsewhere on the board
P0.8: U3.H1 (TMS-SWDIO/P0.8); also elsewhere on the board
P0.9: U3.H2 (TCK-SWCLK/P0.9); also elsewhere on the board
P0.11: U3.K2 (P0.11); also elsewhere on the board
P4.2: U3.R1 (P4.2/TOUTB); also elsewhere on the board

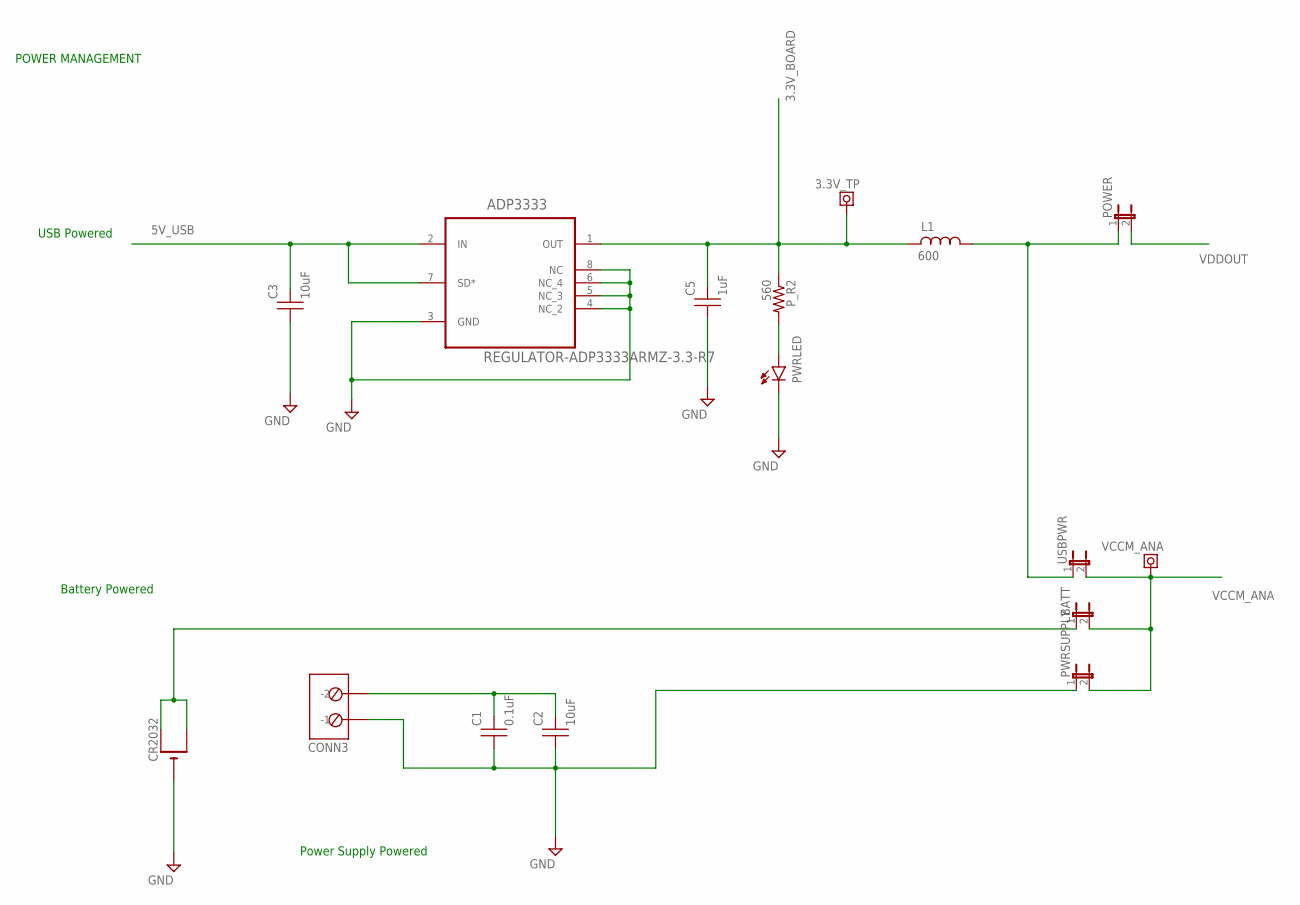
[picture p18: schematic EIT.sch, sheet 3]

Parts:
3.3V_TP: TEST_POINT-TEST_POINTMINI; TP-MINI; MPN H2173-05
ADP3333: REGULATOR-ADP3333ARMZ-3.3-R7; SOP65P490X110-8N
BATT: JUMPER-2PTH; 1X02; MPN M20-9990246
C1: 0.1uF; CAPC1608X87N; PARTNO GRM188R71C104KA01D
C2, C3: 10uF; CAPC1608X87N; PARTNO GRM188R60G106ME47D
C5: 1uF; CAPC1608X87N; PARTNO GRM188R60J105KA01D
CONN3: MKDSN2; PARTNO 1729128
CR2032: CR2032SMT; CR2032-SMD; PARTNO 3002TR
L1: 600; CAPC1608X87N; PARTNO BLM18HG601SN1D
POWER: JUMPER-2PTH; 1X02; MPN M20-9990246
PWRLED: LED-0603; 0603_LED; MPN HSML-C191
PWRSUPPLY: JUMPER-2PTH; 1X02; MPN M20-9990246
P_R2: 560; RES1608X55; MPN CRCW0603560RFKEA
USBPWR: JUMPER-2PTH; 1X02; MPN M20-9990246
VCCM_ANA: TEST_POINT-TEST_POINTMINI; TP-MINI; MPN H2173-05

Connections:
3.3V_BOARD: ADP3333.1 (OUT), C5.2, P_R2.2; also elsewhere on the board
5V_USB: ADP3333.2 (IN), ADP3333.7 (SD*), C3.2; also elsewhere on the board
GND: ADP3333.3 (GND), ADP3333.4 (NC_2), ADP3333.5 (NC_3), ADP3333.6 (NC_4), ADP3333.8 (NC), C1.1, C2.1, C3.1, C5.1, CONN3.1 (-1), CR2032.-, PWRLED.C, PWRSUPPLY.1; also elsewhere on the board
unnamed: PWRLED.A, P_R2.1
unnamed: 3.3V_TP.1, L1.1
unnamed: L1.2, POWER.1, USBPWR.1
unnamed: BATT.1, CR2032.+$1 (+), CR2032.+$2 (+1)
unnamed: C1.2, C2.2, CONN3.2 (-2)
VCCM_ANA: BATT.2, PWRSUPPLY.2, USBPWR.2, VCCM_ANA.1; also elsewhere on the board
VDDOUT: POWER.2; also elsewhere on the board

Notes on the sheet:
POWER MANAGEMENT
USB Powered
Battery Powered
Power Supply Powered

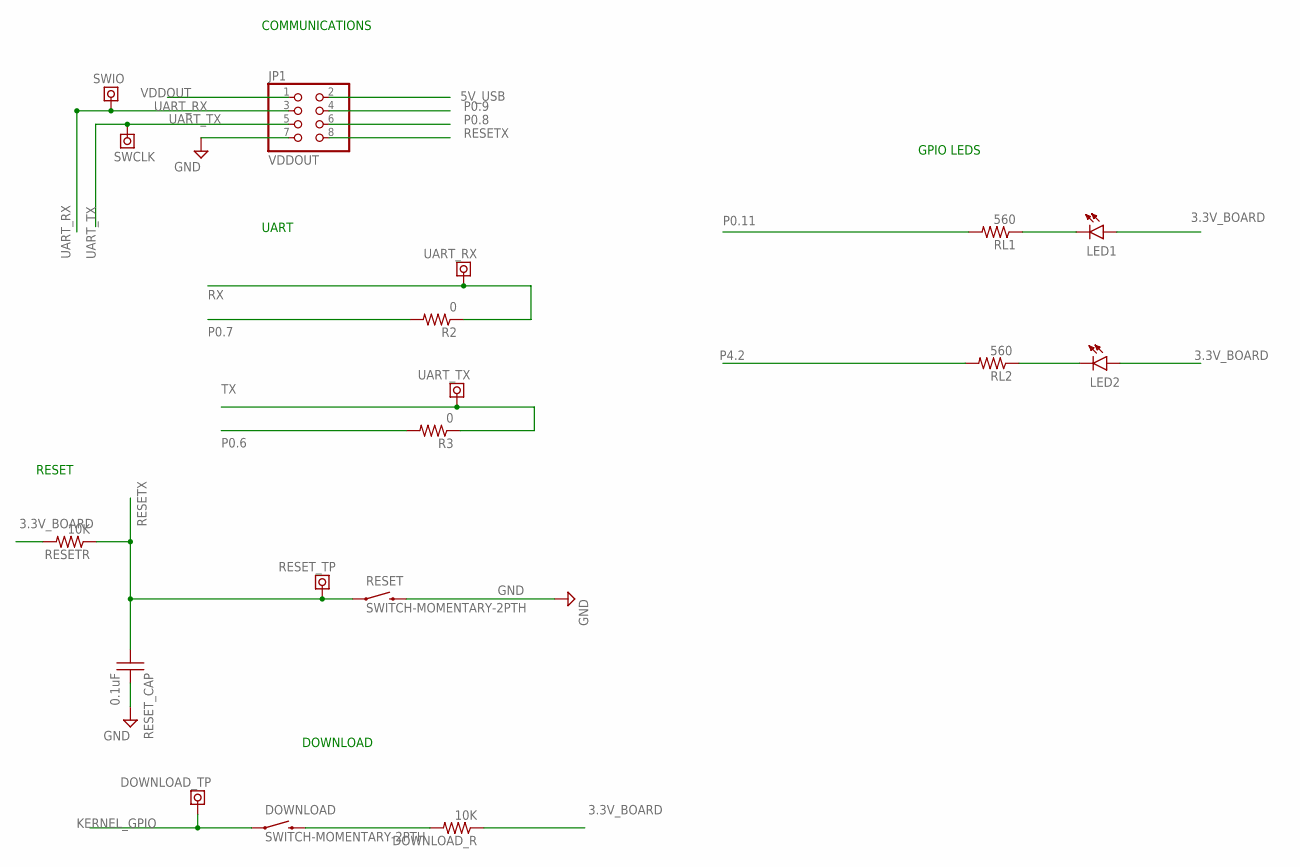
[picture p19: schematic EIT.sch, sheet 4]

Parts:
DOWNLOAD: SWITCH-MOMENTARY-2PTH; TACTILE-PTH; MPN B3S-1000
DOWNLOAD_R: 10K; RES1608X55; MPN MC00625W0402110K
DOWNLOAD_TP: TEST_POINT-TEST_POINTMINI; TP-MINI; MPN H2173-05
JP1: VDDOUT; 2X04/90; MPN 27-12209
LED1: LED-0603; 0603_LED; PARTNO 150060YS75000
LED2: LED-0603; 0603_LED; PARTNO 150060GS75000
R2, R3: 0; RES1608X55; PARTNO MCR03EZPJ000
RESET: SWITCH-MOMENTARY-2PTH; TACTILE-PTH; MPN B3S-1000
RESETR: 10K; RES1608X55; PARTNO MCR03EZPFX1002
RESET_CAP: 0.1uF; CAPC1608X87N; MPN C0805C104J5RACTU
RESET_TP: TEST_POINT-TEST_POINTMINI; TP-MINI; MPN H2173-05
RL1, RL2: 560; RES1608X55; PARTNO MCR03ERTF5600
SWCLK: TEST_POINT-TEST_POINTMINI; TP-MINI; MPN H2173-05
SWIO: TEST_POINT-TEST_POINTMINI; TP-MINI; MPN H2173-05
UART_RX: TEST_POINT-TEST_POINTMINI; TP-MINI; MPN H2173-05
UART_TX: TEST_POINT-TEST_POINTMINI; TP-MINI; MPN H2173-05

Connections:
3.3V_BOARD: DOWNLOAD_R.2, LED1.A, LED2.A, RESETR.1; also elsewhere on the board
5V_USB: JP1.2; also elsewhere on the board
GND: JP1.7, RESET.3 (2), RESET_CAP.2; also elsewhere on the board
KERNEL_GPIO: DOWNLOAD.1, DOWNLOAD_TP.1; also elsewhere on the board
unnamed: DOWNLOAD.3 (2), DOWNLOAD_R.1
unnamed: LED2.C, RL2.2
unnamed: LED1.C, RL1.2
P0.6: R3.1; also elsewhere on the board
P0.7: R2.1; also elsewhere on the board
P0.8: JP1.6; also elsewhere on the board
P0.9: JP1.4; also elsewhere on the board
P0.11: RL1.1; also elsewhere on the board
P4.2: RL2.1; also elsewhere on the board
RESETX: JP1.8, RESET.1, RESETR.2, RESET_CAP.1, RESET_TP.1; also elsewhere on the board
RX: R2.2, UART_RX.1; also elsewhere on the board
TX: R3.2, UART_TX.1; also elsewhere on the board
UART_RX: JP1.3, SWIO.1; also elsewhere on the board
UART_TX: JP1.5, SWCLK.1; also elsewhere on the board
VDDOUT: JP1.1; also elsewhere on the board

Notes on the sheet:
COMMUNICATIONS
UART
DOWNLOAD
RESET
GPIO LEDS

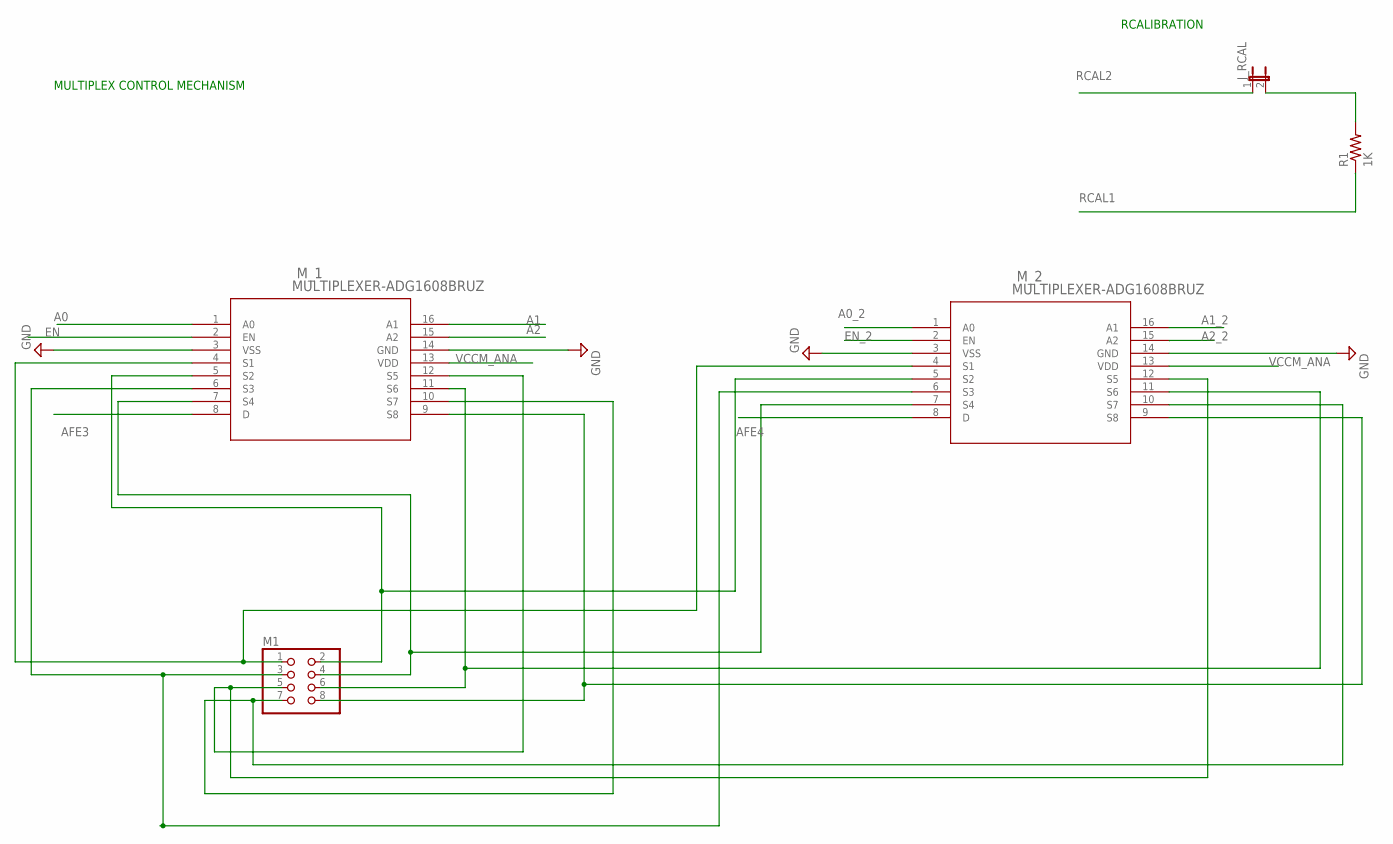
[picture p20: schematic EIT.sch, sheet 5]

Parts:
J_RCAL: JUMPER-2PTH; 1X02; MPN M20-9990246
M1: PINHD-2X42X04SHROUDED; 2X04SHROUDED; PARTNO 3020-08-0200-02
M_1, M_2: MULTIPLEXER-ADG1608BRUZ; RU_16; PARTNO ADG1608BRUZ
R1: 1K; 0603-RES; MPN ERJ-3EKF1001V

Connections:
A0: M_1.1 (A0); also elsewhere on the board
A0_2: M_2.1 (A0); also elsewhere on the board
A1: M_1.16 (A1); also elsewhere on the board
A1_2: M_2.16 (A1); also elsewhere on the board
A2: M_1.15 (A2); also elsewhere on the board
A2_2: M_2.15 (A2); also elsewhere on the board
AFE3: M_1.8 (D); also elsewhere on the board
AFE4: M_2.8 (D); also elsewhere on the board
EN: M_1.2 (EN); also elsewhere on the board
EN_2: M_2.2 (EN); also elsewhere on the board
GND: M_1.3 (VSS), M_1.14 (GND), M_2.3 (VSS), M_2.14 (GND); also elsewhere on the board
M2_1: M1.1, M_1.4 (S1), M_2.4 (S1)
M2_2: M1.2, M_1.5 (S2), M_2.5 (S2)
M2_3: M1.3, M_1.6 (S3), M_2.6 (S3)
M2_4: M1.4, M_1.7 (S4), M_2.7 (S4)
M2_7: M1.7, M_1.10 (S7), M_2.10 (S7)
M2_8: M1.8, M_1.9 (S8), M_2.9 (S8)
unnamed: M1.5, M_1.12 (S5), M_2.12 (S5)
unnamed: J_RCAL.2, R1.2
unnamed: M1.6, M_1.11 (S6), M_2.11 (S6)
RCAL1: R1.1; also elsewhere on the board
RCAL2: J_RCAL.1; also elsewhere on the board
VCCM_ANA: M_1.13 (VDD), M_2.13 (VDD); also elsewhere on the board

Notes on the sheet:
MULTIPLEX CONTROL MECHANISM
RCALIBRATION

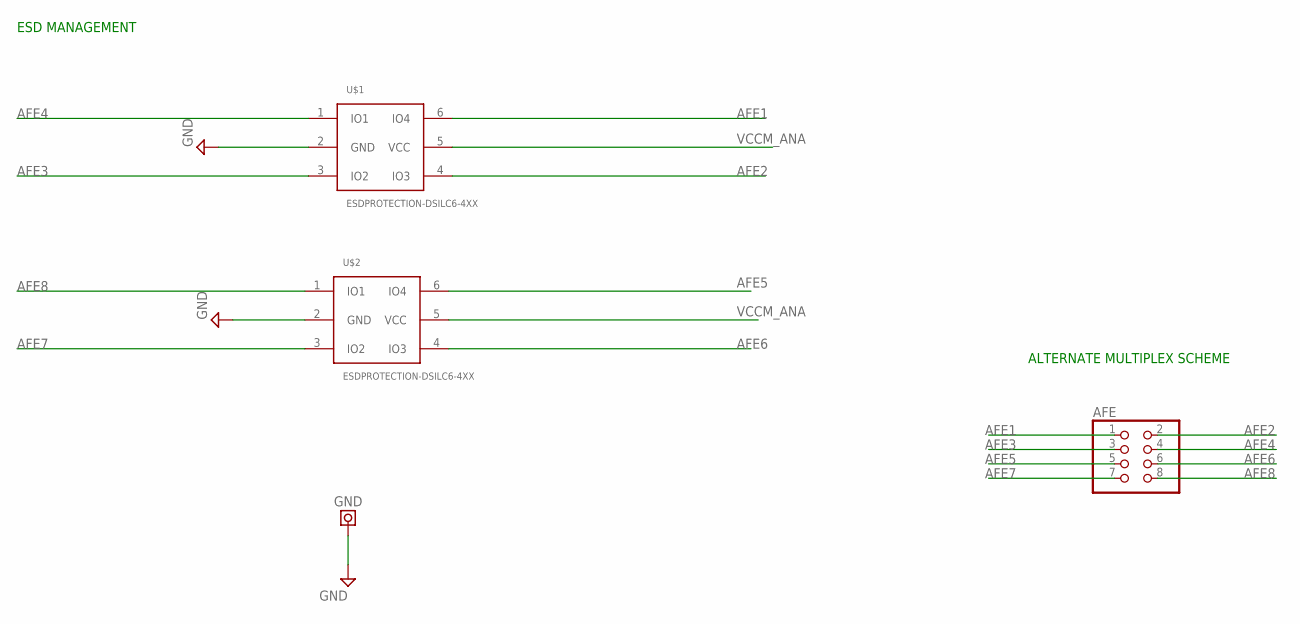
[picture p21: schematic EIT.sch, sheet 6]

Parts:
AFE: PINHD-2X42X04SHROUDED; 2X04SHROUDED; PARTNO 3020-08-0200-02
GND: TEST_POINT-TEST_POINTMINI; TP-MINI; PARTNO 5003
U$1, U$2: ESDPROTECTION-DSILC6-4XX; SOT-666; MPN DSILC6-4P6

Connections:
AFE1: AFE.1, U$1.6 (IO4); also elsewhere on the board
AFE2: AFE.2, U$1.4 (IO3); also elsewhere on the board
AFE3: AFE.3, U$1.3 (IO2); also elsewhere on the board
AFE4: AFE.4, U$1.1 (IO1); also elsewhere on the board
AFE5: AFE.5, U$2.6 (IO4); also elsewhere on the board
AFE6: AFE.6, U$2.4 (IO3); also elsewhere on the board
AFE7: AFE.7, U$2.3 (IO2); also elsewhere on the board
AFE8: AFE.8, U$2.1 (IO1); also elsewhere on the board
GND: GND.1, U$1.2 (GND), U$2.2 (GND); also elsewhere on the board
VCCM_ANA: U$1.5 (VCC), U$2.5 (VCC); also elsewhere on the board

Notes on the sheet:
ESD MANAGEMENT
ALTERNATE MULTIPLEX SCHEME

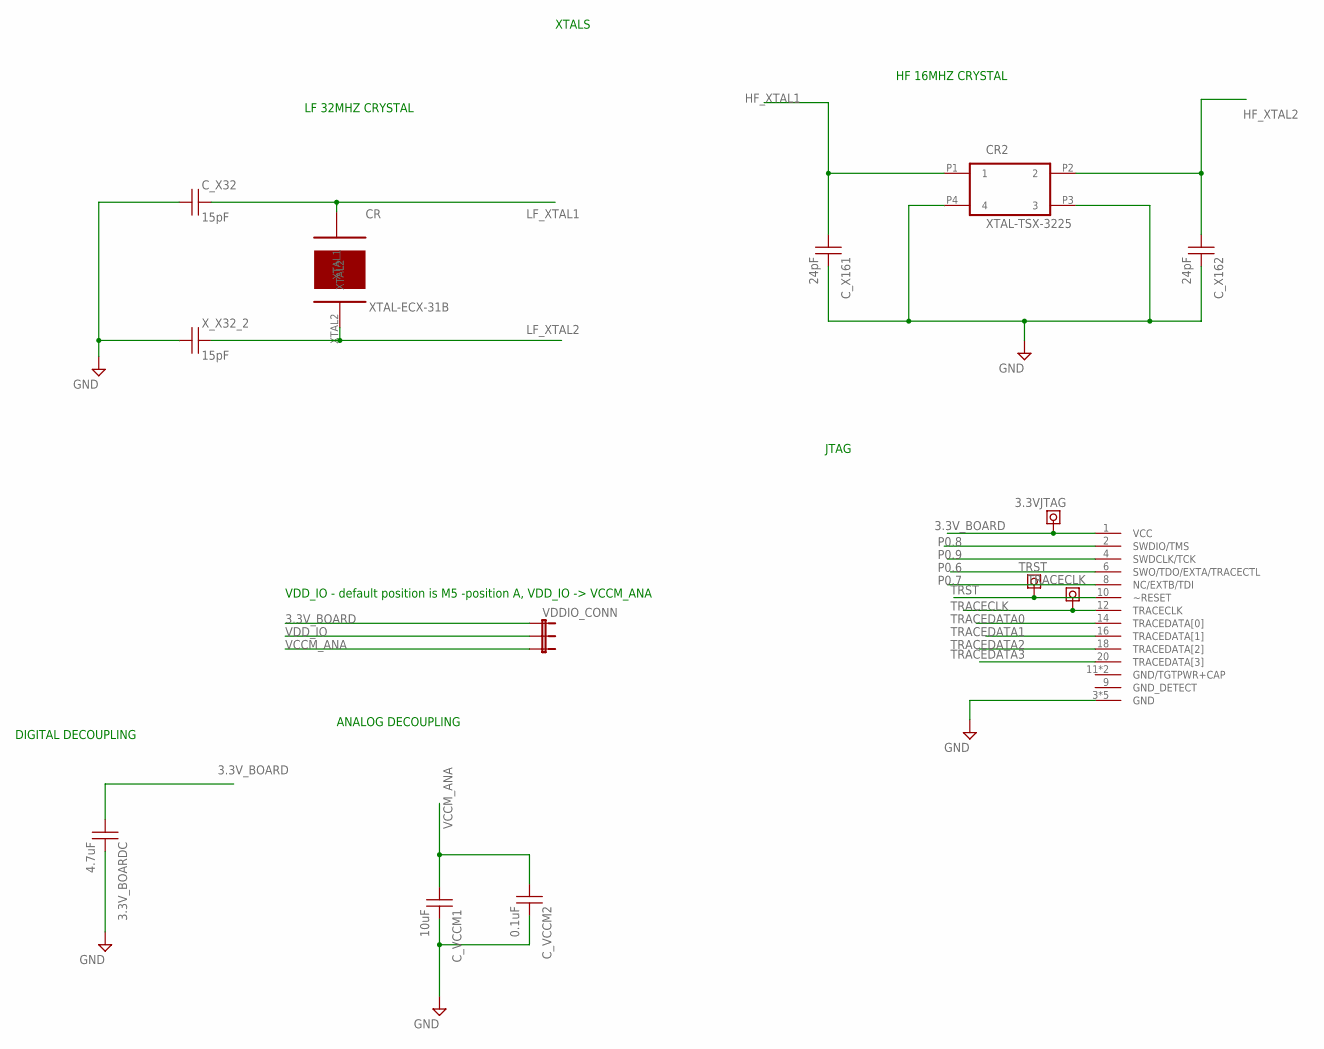
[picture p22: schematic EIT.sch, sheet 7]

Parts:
3.3VJTAG: TEST_POINT-TEST_POINTMINI; TP-MINI; PARTNO 5003
3.3V_BOARDC: 4.7uF; CAPC1608X87N; MPN GRM188R60J475ME19D
CR: XTAL-ECX-31B; PARTNO ECS-.327-7-34B-TR
CR2: XTAL-TSX-3225; TSX-3225; PARTNO FA-238 16.0000MB-K3
C_VCCM1: 10uF; CAPC1608X87N; MPN C0805C106Z8VACTU
C_VCCM2: 0.1uF; CAPC1608X87N; MPN MC0402X104K100CT
C_X32: 15pF; CAPC1608X87N; MPN GRM188R60J475ME19D
C_X161, C_X162: 24pF; CAPC1608X87N; MPN MC0402X104K100CT
TRACECLK: TEST_POINT-TEST_POINTMINI; TP-MINI; PARTNO 5003
TRST: TEST_POINT-TEST_POINTMINI; TP-MINI; PARTNO 5003
U$11: 2X10_0.05"_CORTEX_DEBUG_WITH_ETMSMD_SHROUDED; 2X10_0.05"_SMD_SH; PARTNO EHF-110-01-L-D-SM
VDDIO_CONN: JUMPER-3PTH; 1X03; MPN M20-9990345
X_X32_2: 15pF; CAPC1608X87N; MPN GRM188R60J475ME19D

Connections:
3.3V_BOARD: 3.3VJTAG.1, 3.3V_BOARDC.1, U$11.1 (VCC), VDDIO_CONN.1; also elsewhere on the board
GND: 3.3V_BOARDC.2, CR2.P3 (3), CR2.P4 (4), C_VCCM1.2, C_VCCM2.2, C_X32.1, C_X161.2, C_X162.2, U$11.3 (GND), U$11.5 (GND), U$11.15 (GND), U$11.17 (GND), U$11.19 (GND), X_X32_2.1; also elsewhere on the board
HF_XTAL1: CR2.P1 (1), C_X161.1; also elsewhere on the board
HF_XTAL2: CR2.P2 (2), C_X162.1; also elsewhere on the board
LF_XTAL1: CR.XTAL1, C_X32.2; also elsewhere on the board
LF_XTAL2: CR.XTAL2, X_X32_2.2; also elsewhere on the board
P0.6: U$11.6 (SWO/TDO/EXTA/TRACECTL); also elsewhere on the board
P0.7: U$11.8 (NC/EXTB/TDI); also elsewhere on the board
P0.8: U$11.2 (SWDIO/TMS); also elsewhere on the board
P0.9: U$11.4 (SWDCLK/TCK); also elsewhere on the board
TRACECLK: TRACECLK.1, U$11.12 (TRACECLK); also elsewhere on the board
TRACEDATA0: U$11.14 (TRACEDATA[0]); also elsewhere on the board
TRACEDATA1: U$11.16 (TRACEDATA[1]); also elsewhere on the board
TRACEDATA2: U$11.18 (TRACEDATA[2]); also elsewhere on the board
TRACEDATA3: U$11.20 (TRACEDATA[3]); also elsewhere on the board
TRST: TRST.1, U$11.10 (~RESET); also elsewhere on the board
VCCM_ANA: C_VCCM1.1, C_VCCM2.1, VDDIO_CONN.3; also elsewhere on the board
VDD_IO: VDDIO_CONN.2; also elsewhere on the board

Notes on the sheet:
VDD_IO - default position is M5 -position A, VDD_IO -> VCCM_ANA
DIGITAL DECOUPLING
ANALOG DECOUPLING
JTAG
XTALS
LF 32MHZ CRYSTAL
HF 16MHZ CRYSTAL

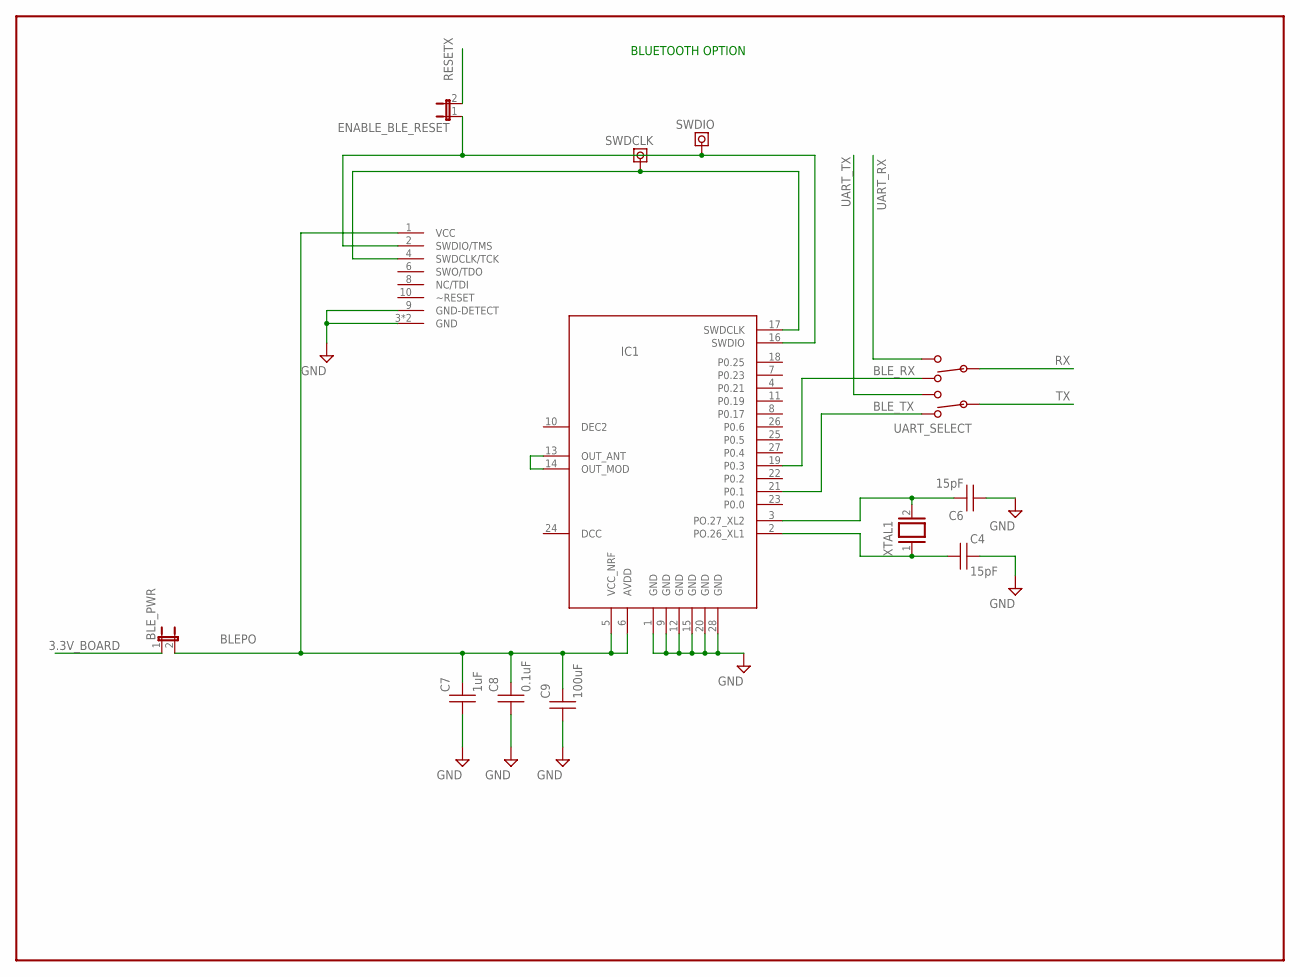
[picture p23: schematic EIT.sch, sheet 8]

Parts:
BLE_PWR: JUMPER-2PTH; 1X02; PARTNO M20-9990246
C4, C6: 15pF; CAPC1608X87N; PARTNO GRM1885C1H150JA01D
C7: 1uF; CAPC1608X87N; PARTNO GRM188R60J105KA01D
C8: 0.1uF; CAPC1608X87N; PARTNO GRM188R71C104KA01D
C9: 100uF; CAP2012X100N; PARTNO GRM21BR60G107ME15L
ENABLE_BLE_RESET: JUMPER-2PTH; 1X02; PARTNO M20-9990246
IC1: TY-EYSGJNAWY-1X; TY-EYSGJN; PARTNO EYSGJNAWY-1X
SWDCLK: TEST_POINT-TEST_POINTMINI; TP-MINI; PARTNO 5003
SWDIO: TEST_POINT-TEST_POINTMINI; TP-MINI; PARTNO 5003
U$10: 2X5_0.05"_CORTEX_DEBUGSMD_SHROUDED; 2X5_0.05"_SMD_SH; PARTNO SHF-105-01-L-D-SM-LC
UART_SELECT: SWITCH-DPDT; SWITCH-G13AH; PARTNO G22AP
XTAL1: XTAL_BLE-2-SMD; FC-12M; PARTNO SER3673CT-ND

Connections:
3.3V_BOARD: BLE_PWR.1; also elsewhere on the board
BLEPO: BLE_PWR.2, C7.2, C8.2, C9.2, IC1.5 (VCC_NRF), IC1.6 (AVDD), U$10.1 (VCC)
BLE_RX: IC1.19 (P0.3), UART_SELECT.1
BLE_TX: IC1.21 (P0.1), UART_SELECT.4
GND: C4.2, C6.1, C7.1, C8.1, C9.1, IC1.1 (GND), IC1.9 (GND), IC1.12 (GND), IC1.15 (GND), IC1.20 (GND), IC1.28 (GND), U$10.3 (GND), U$10.5 (GND), U$10.9 (GND-DETECT); also elsewhere on the board
unnamed: IC1.13 (OUT_ANT), IC1.14 (OUT_MOD)
unnamed: C4.1, IC1.2 (PO.26_XL1), XTAL1.1
unnamed: C6.2, IC1.3 (PO.27_XL2), XTAL1.2
unnamed: IC1.17 (SWDCLK), SWDCLK.1, U$10.4 (SWDCLK/TCK)
unnamed: ENABLE_BLE_RESET.1, IC1.16 (SWDIO), SWDIO.1, U$10.2 (SWDIO/TMS)
RESETX: ENABLE_BLE_RESET.2; also elsewhere on the board
RX: UART_SELECT.2; also elsewhere on the board
TX: UART_SELECT.5; also elsewhere on the board
UART_RX: UART_SELECT.3; also elsewhere on the board
UART_TX: UART_SELECT.6; also elsewhere on the board

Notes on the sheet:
BLUETOOTH OPTION

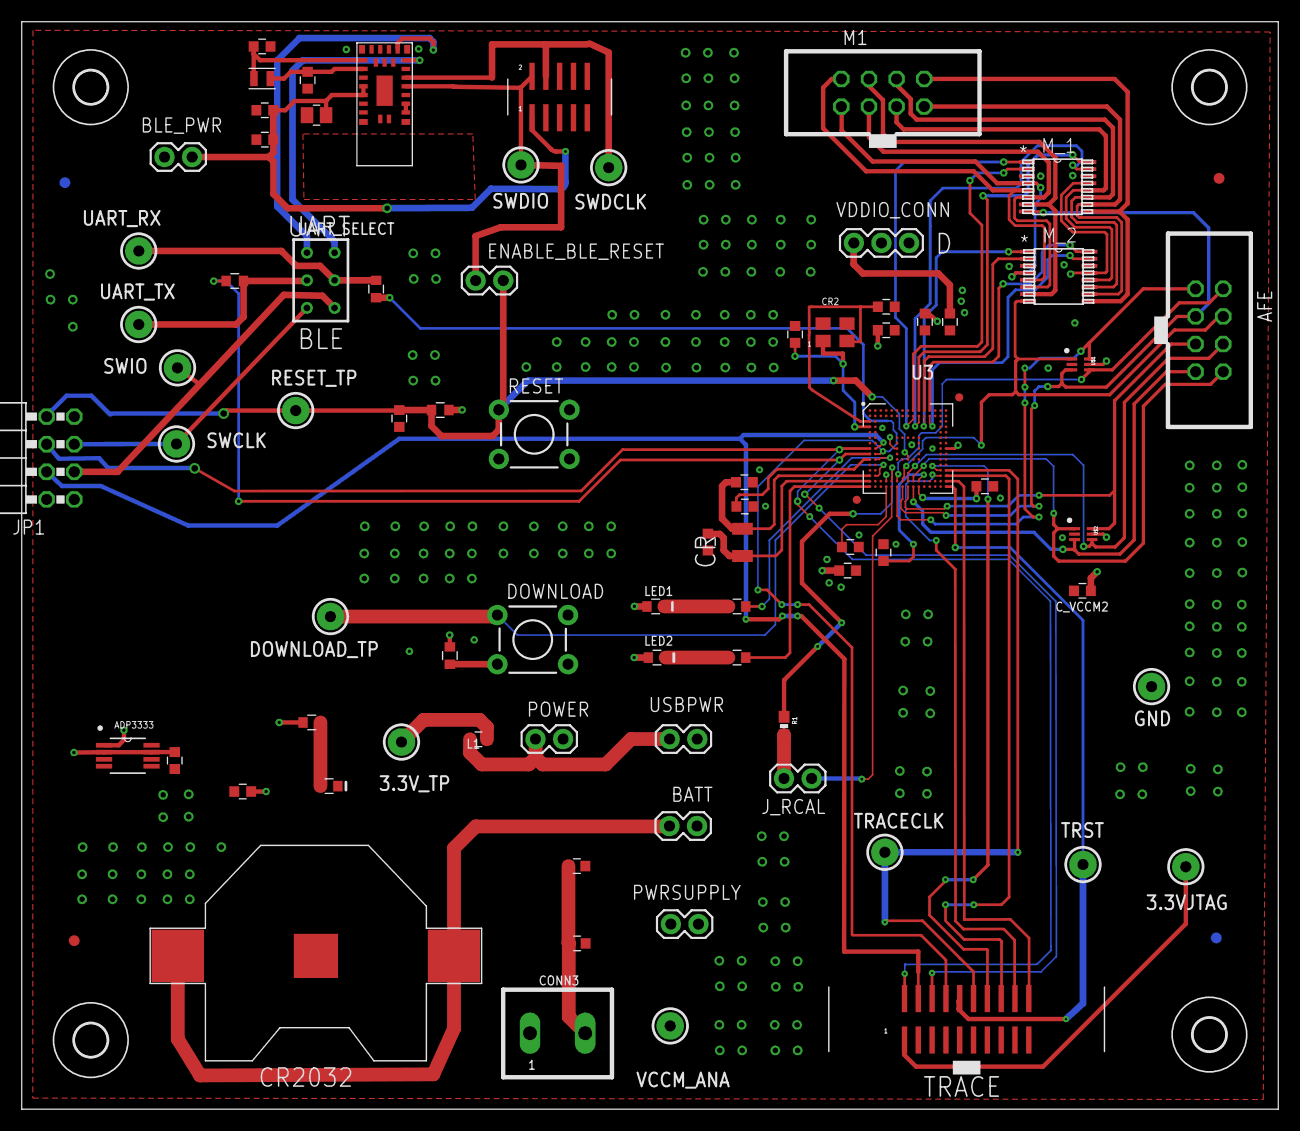
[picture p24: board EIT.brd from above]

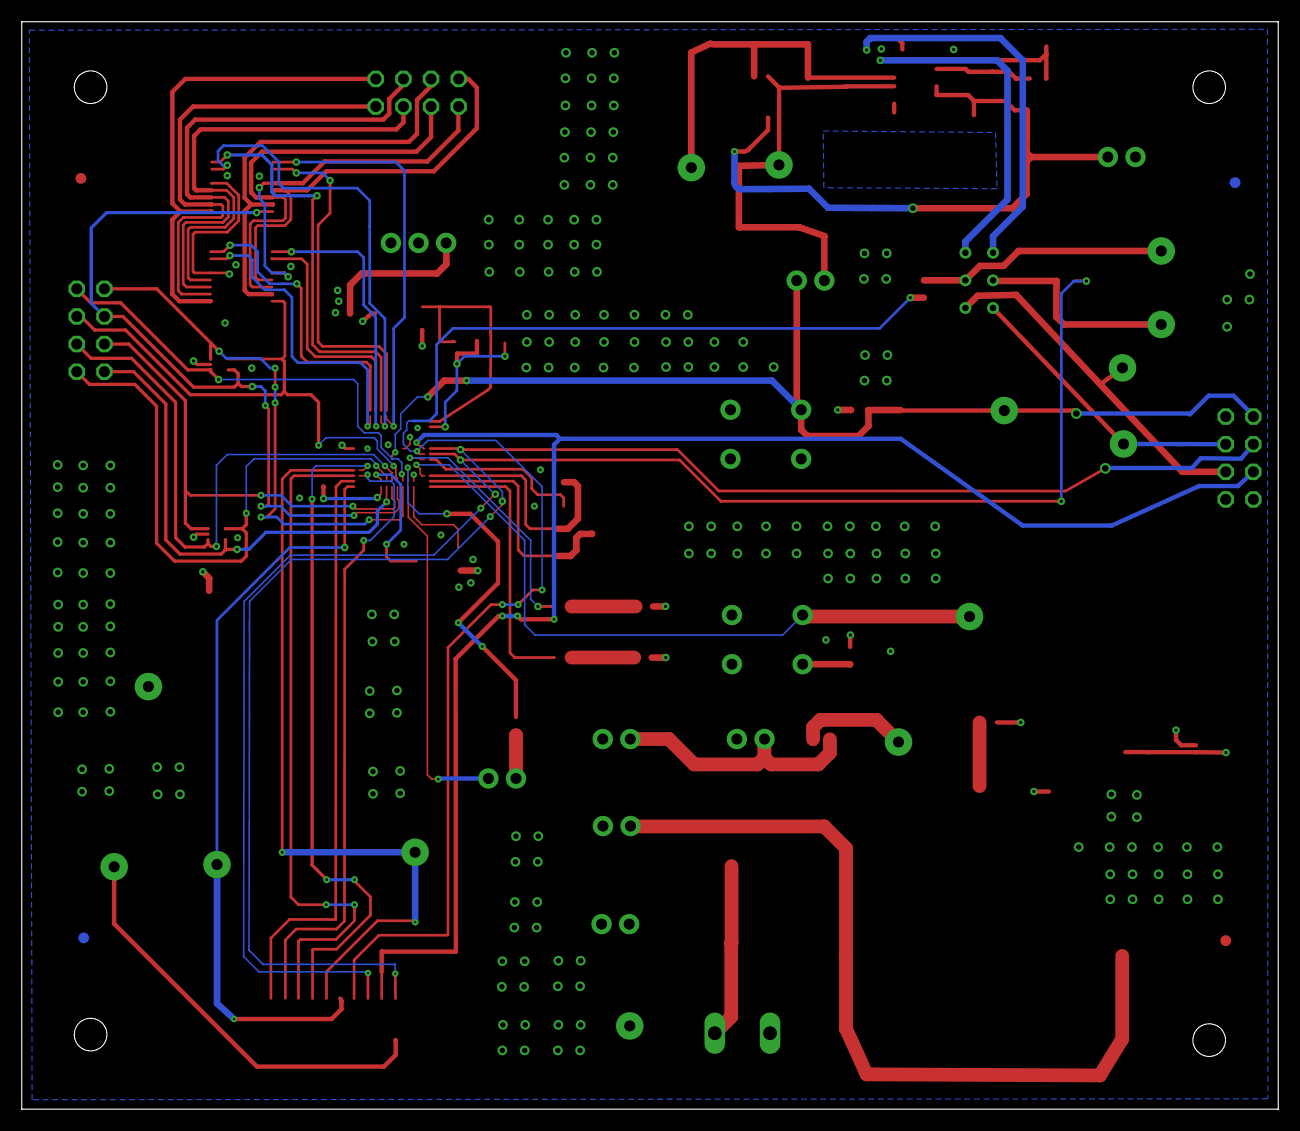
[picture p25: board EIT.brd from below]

Board: 4 copper layers, 115.5 x 100.0 mm, 85 parts (2 on the bottom side), 76 nets.

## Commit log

2017-11-22 8 electrode EIT system
    [EIT.GBL, EIT.GBS, EIT.GKO, EIT.GTL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]
2019-04-08 8 electrode flex gerbers added
    [eit.kicad_pcb]

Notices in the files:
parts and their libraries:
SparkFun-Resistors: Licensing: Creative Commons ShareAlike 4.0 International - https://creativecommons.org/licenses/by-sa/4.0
